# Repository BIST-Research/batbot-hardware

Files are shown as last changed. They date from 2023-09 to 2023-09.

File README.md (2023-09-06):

# batbot-hardware
schematics and pcbs for the batbot

## batbot-6.5 wiring diagram
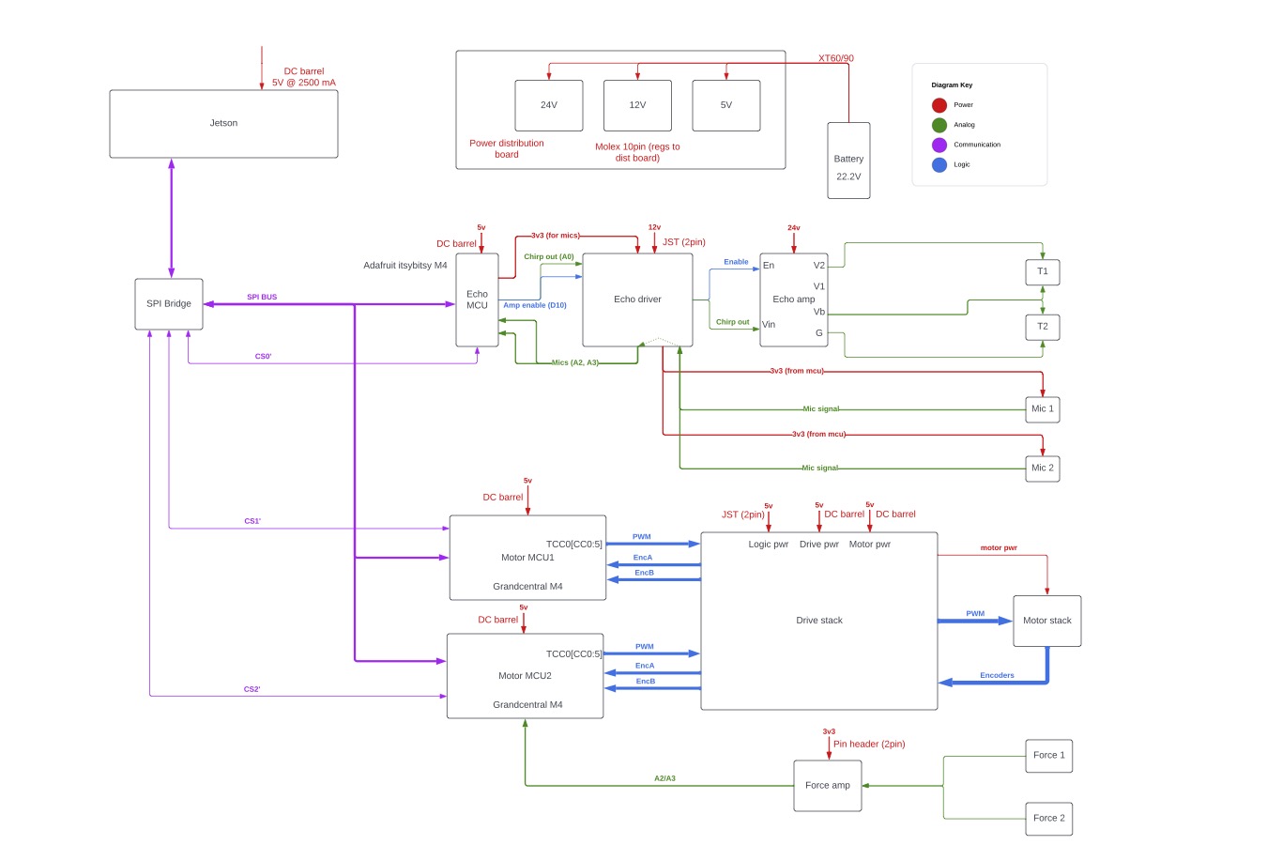
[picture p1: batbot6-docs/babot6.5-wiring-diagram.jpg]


## Adafruit itsybitsy M4 pinout
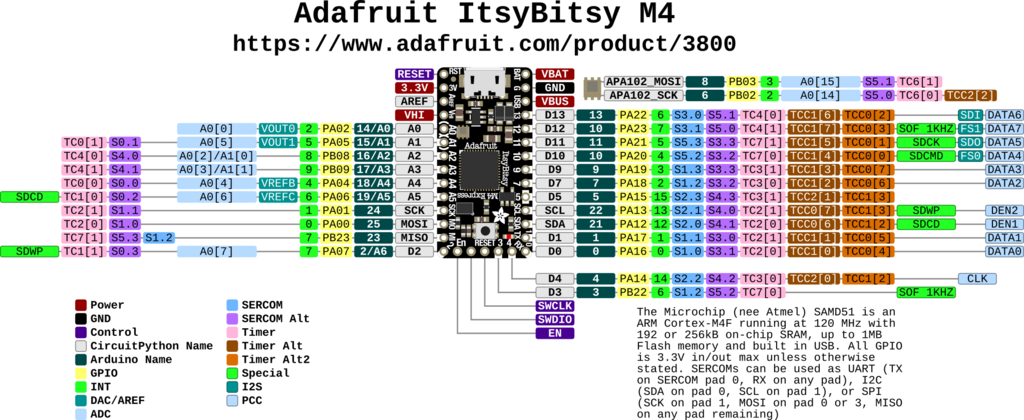
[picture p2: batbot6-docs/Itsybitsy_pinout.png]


## Grandcentral M4 pinout
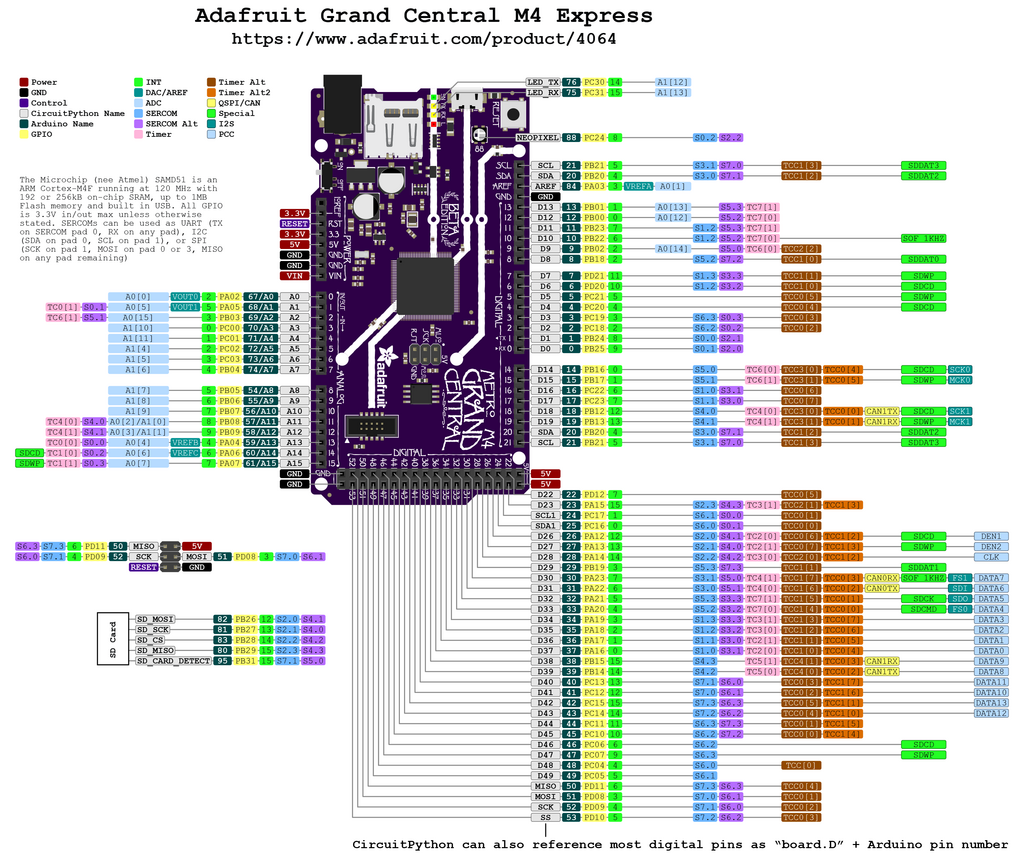
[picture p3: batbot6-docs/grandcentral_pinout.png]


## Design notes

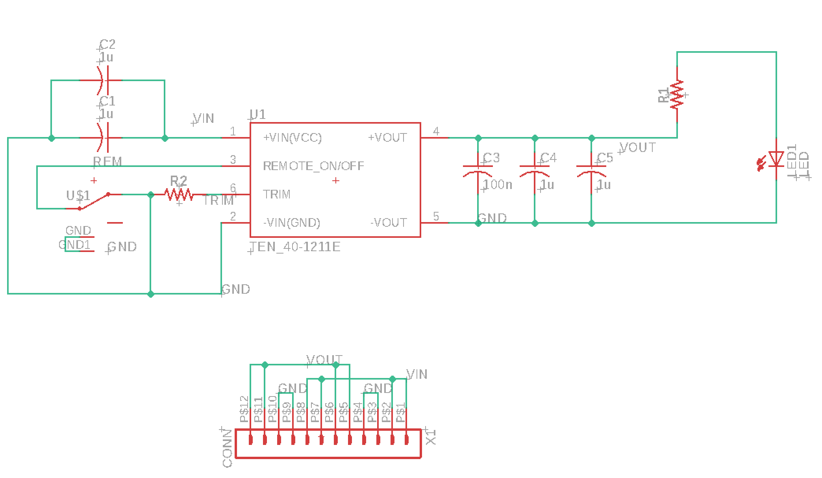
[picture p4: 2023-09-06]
batbot6-power/pc_3v3_rev2/Screen Shot 2023-04-12 at 1.07.49 PM.png

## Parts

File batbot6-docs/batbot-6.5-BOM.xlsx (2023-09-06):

General | Item | Qty | ext price | total price | Link
 | Adafruit Grandcentral M4 | 2 | 39.99 | 79.98 | https://www.adafruit.com/grandcentral
 | Adafruit ItsyBitsy M4 | 1 | 14.95 | 14.95 | https://www.adafruit.com/product/3800
 | Dodotroninc Momimic | 2 | 128.73 | 257.46 | https://www.dodotronic.com/product/momimic/
 | PDm200 V9 | 1 | 296 | 296 | https://www.piezodrive.com/modules/pdm200/
 | 604144 Ultrasonic Transducer | 2 | 30.15 | 60.3 | https://senscomp.com/product/pid-604144-series-600-open-face-ultrasonic-sensor/
 | Nvidia Jetson Nano | 1 | 149 | 149 | https://a.co/d/4efK6vB
 | M2.5 standoff kit | 1 | 14.69 | 14.69 | https://a.co/d/06DHvGg
 | JST male- -> female precrimped kit | 1 | 24.99 | 24.99 | https://a.co/d/bxBMKHO
 | JST female -> female precrimped kit | 1 | 23.99 | 23.99 | https://a.co/d/cVUfNm2
 | JST single ended kit | 1 | 11.99 | 11.99 | https://a.co/d/iteqkm4
Power
 | TEN40-2412E | 1 | 63.89 | 63.89 | https://www.mouser.com/ProductDetail/TRACO-Power/TEN-40-2412E?qs=BJlw7L4Cy78h%252BnAvaMysmw%3D%3D
 | TEN40-2415E | 1 | 62.63 | 62.63 | https://www.mouser.com/ProductDetail/TRACO-Power/TEN-40-2415E?qs=BJlw7L4Cy78izuCDjrMfuQ%3D%3D
 | TEN40-2411E | 1 | 64.85 | 64.85 | https://www.mouser.com/ProductDetail/TRACO-Power/TEN-40-2411E?qs=BJlw7L4Cy79nArvdbUqL%252BA%3D%3D
 | Molex 12 pin female | 3 | 3.9 | 11.7 | https://www.mouser.com/ProductDetail/Molex/44432-1201?qs=WqOAika8Ruu6VDg3%252BKMCCQ%3D%3D
 | Molex 12 pin male | 3 | 5.42 | 16.26 | https://www.mouser.com/ProductDetail/Molex/44764-1201?qs=2RatRY%252BUrpFLNA1OlZuacA%3D%3D
 | XT-60 female | 1 | 1.5 | 1.5 | https://www.mouser.com/ProductDetail/SparkFun/PRT-10474?qs=WyAARYrbSnYJaRDMiD9g2w%3D%3D
 | ZeePower 6000 mAh lipo | 1 | 84.99 | 84.99 | https://a.co/d/9gDvzcF
 | 1825232-1 slide switch | 3 | 0.37 | 1.11 | https://www.mouser.com/ProductDetail/TE-Connectivity-PB/1825232-1?qs=kTKVN3NWb5FosGxaNC1%252BtA%3D%3D
Motors
 | DRV8833 motor driver | 6 | 9.15 | 54.9 | https://www.pololu.com/product/2130
 | 6V 100:1 dc gear motor | 12 | 18.35 | 220.2 | https://www.pololu.com/product/992
 | magnetic encoder pairs | 6 | 7.31 | 43.86 | https://www.pololu.com/product/4760
 | 6 pin female JST SH | 12 | 2.2 | 26.4 | https://www.pololu.com/product/4766
 | JST SH TH breakout adapter | 12 | 1.15 | 13.8 | https://www.pololu.com/product/4772
 | LDTM-028K PVDF | 2 | 6.84 | 13.68 | https://www.mouser.com/ProductDetail/Measurement-Specialties/LDTM-028K?qs=Pz4gaf3%252B8zwC7TEQph04jQ%3D%3D&mgh=1

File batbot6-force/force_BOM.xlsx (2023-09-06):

Desc | Value | Designator | Footprint | part # | type
Cap 50V cer 10% | 10n | C1,C2 | 1206 | C1846 | basic
Cap 50V cer 10% | 100n | C3,C4,C5 | 1206 | C1946 | basic
Res 100mW 1% | 22k | R1,R2 | 0603 | C31850 | basic
Res 100mW 1% | 2k7 | R6,R7 | 0603 | C13167 | basic
Res 100mW 1% | 1Meg | R4,R5,R8,R9 | 0603 | C22935 | basic

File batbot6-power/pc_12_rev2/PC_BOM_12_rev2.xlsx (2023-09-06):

Desc | Value | Designator | Footprint | part # | type
Cap 50V cer 10% | 1u | C1,C2,C4,C5 | 1206 | C1848 | basic
Cap 50V cer 10% | 0u1 | C3 | 1206 | C24497 | basic
Res 250mW 1% | 2k | R1 | 1206 | C17936 | basic
Res 250mW 1% | 200k | R2 | 1206 | C352122 | extended

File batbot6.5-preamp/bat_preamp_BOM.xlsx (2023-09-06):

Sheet: caps
Capacitors
Designator | Value | Package | Tolerance (%) | Usage | Rating (VDC) | ESR (Ohms) | Type | Link
C1 | 10u | 3528 (KEMET-B) | 10 | PSD | 20 | 2.1 | Tantalum | https://www.mouser.com/ProductDetail/KEMET/T491B106K020AT?qs=WydH9nGI6cCRyexXwG9dQg%3D%3D
C2 | 0u1 | 3216 (KEMET-A) | 10 | PSD | 35 | 20 | Tantalum | https://www.mouser.com/ProductDetail/KEMET/T491A104K035AT?qs=VCf6WUQjPgHZen45Mmzj1w%3D%3D
C3 | 0u1 | 3216 (KEMET-A) | 10 | PSD | 35 | 20 | Tantalum | https://www.mouser.com/ProductDetail/KEMET/T491A104K035AT?qs=VCf6WUQjPgHZen45Mmzj1w%3D%3D
C4 | 3u3 | 3216 (KEMET-A) | 10 | PSD | 25 | 0.045 | Tantalum | https://www.mouser.com/ProductDetail/KEMET/T491A335K025AT?qs=PquRuO%2FYcjpqg96tM3ceqQ%3D%3D
C5 | 22u | 6032 (KEMET-C) | 10 | PSD | 25 | 1.4 | Tantalum | https://www.mouser.com/ProductDetail/KEMET/T491C226K025AT
C6 | 0u1 | 3216 (KEMET-A) | 10 | PSD | 35 | 20 | Tantalum | https://www.mouser.com/ProductDetail/KEMET/T491A104K035AT?qs=VCf6WUQjPgHZen45Mmzj1w%3D%3D
C7 | 100n | 0402 | 10 | SIG | 16 | ? | MLCC | https://www.mouser.com/ProductDetail/TDK/C1005X7R1C104K050BC?qs=NRhsANhppD%252BhAGOapA8QKQ%3D%3D
C8 | 100n | 0402 | 10 | SIG | 16 | ? | MLCC | https://www.mouser.com/ProductDetail/TDK/C1005X7R1C104K050BC?qs=NRhsANhppD%252BhAGOapA8QKQ%3D%3D
C9 | 10n | 0402 | 10 | SIG | 25 | ? | MLCC | https://www.mouser.com/ProductDetail/TDK/C1005X7R1E103K050BB?qs=NRhsANhppD8434p4mMcNYg%3D%3D
C10 | 10n | 0402 | 10 | SIG | 25 |  | MLCC | https://www.mouser.com/ProductDetail/TDK/C1005X7R1E103K050BB?qs=NRhsANhppD8434p4mMcNYg%3D%3D

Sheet: diodes
Diodes
Designator | Value | Package | Vf (V) | If (mA) | Usage | Link
D1 | PWR_IND | 1608 | 2 | 20 | LED | https://www.mouser.com/ProductDetail/Wurth-Elektronik/150060AS75003?qs=Li%252BoUPsLEntY15YiEuZJ2w%3D%3D
D2 | JOB_IND | 1608 | 2.85 | 20 | LED | https://www.mouser.com/ProductDetail/Vishay-Semiconductors/VLMTG1400-GS08?qs=gt1LBUVyoHlZ6yHd8iEIzQ%3D%3D

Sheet: conn
Connectors
Designator | Value | Package | Type | Link
J1 | m4_conn_pwr | JST_XH_B4B_Vertical | PWR
J2 | amp_conn_pwr | JST_XH_B4B_Vertical | PWR
J3 | force_conn_in | JST_XH_B4B_Vertical | SIG
J4 | echo_conn_in | JST_XH_B7B_Vertical | SIG
J5 | mic_conn_r | JST_XH_B5B_Vertical | SIG
J6 | mic_conn_l | JST_XH_B5B_Vertical | SIG
J7 | amp_conn_out | JST_XH_B2B_Vertical | SIG
J8 | force_conn_out | JST_XH_B2B_Vertical | SIG

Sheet: res
Resistors
Designator | Value | Package | Tolerance (%) | Rating (W) | Link
R1 | 500R | 3216 | 0.05 | 0.25 | https://www.mouser.com/ProductDetail/Vishay-Draloric/TNPU1206500RAZEN00
R2 | 500R | 3216 | 0.05 | 0.25 | https://www.mouser.com/ProductDetail/Vishay-Draloric/TNPU1206500RAZEN00
R3 | 12k | 3216 | 0.1 | 0.25 | https://www.mouser.com/ProductDetail/Panasonic/ERA-8VRB1202V
R4 | 10k | 3216 | 0.1 | 0.25 | https://www.mouser.com/ProductDetail/Panasonic/ERA-8VRB1002V
R5 | 39k | 3216 | 0.1 | 0.25 | https://www.mouser.com/ProductDetail/Panasonic/ERA-8VRB3902V
R6 | 27k | 3216 | 0.1 | 0.25 | https://www.mouser.com/ProductDetail/Panasonic/ERA-8VRB2702V
R7 | 10k | 3216 | 0.1 | 0.25 | https://www.mouser.com/ProductDetail/Panasonic/ERA-8VRB1002V
R8 | 100k | 3216 | 0.1 | 0.25 | https://www.mouser.com/ProductDetail/Panasonic/ERA-8VRB1003V
R9 | 2k7 | 3216 | 0.1 | 0.25 | https://www.mouser.com/ProductDetail/Panasonic/ERA-8ARB272V
R10 | 2k7 | 3216 | 0.1 | 0.25 | https://www.mouser.com/ProductDetail/Panasonic/ERA-8ARB272V
R11 | 1Meg | 3216 | 0.1 | 0.25 | https://www.mouser.com/ProductDetail/Panasonic/ERA-8AED105V
R12 | 1Meg | 3216 | 0.1 | 0.25 | https://www.mouser.com/ProductDetail/Panasonic/ERA-8AED105V
R13 | 22k | 3216 | 0.1 | 0.25 | https://www.mouser.com/ProductDetail/Panasonic/ERA-8AEB223V
R14 | 22k | 3216 | 0.1 | 0.25 | https://www.mouser.com/ProductDetail/Panasonic/ERA-8AEB223V

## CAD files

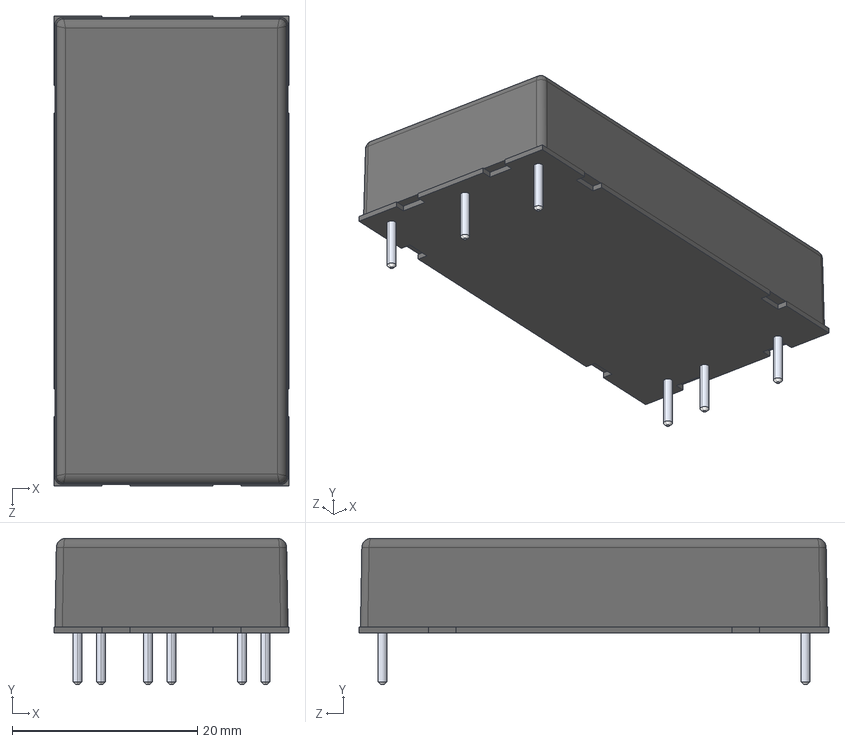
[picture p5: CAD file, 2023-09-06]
batbot6.5-power/TEN_40-2410E/TEN_40-2410E.step
25.4 x 15.8 x 50.8 mm

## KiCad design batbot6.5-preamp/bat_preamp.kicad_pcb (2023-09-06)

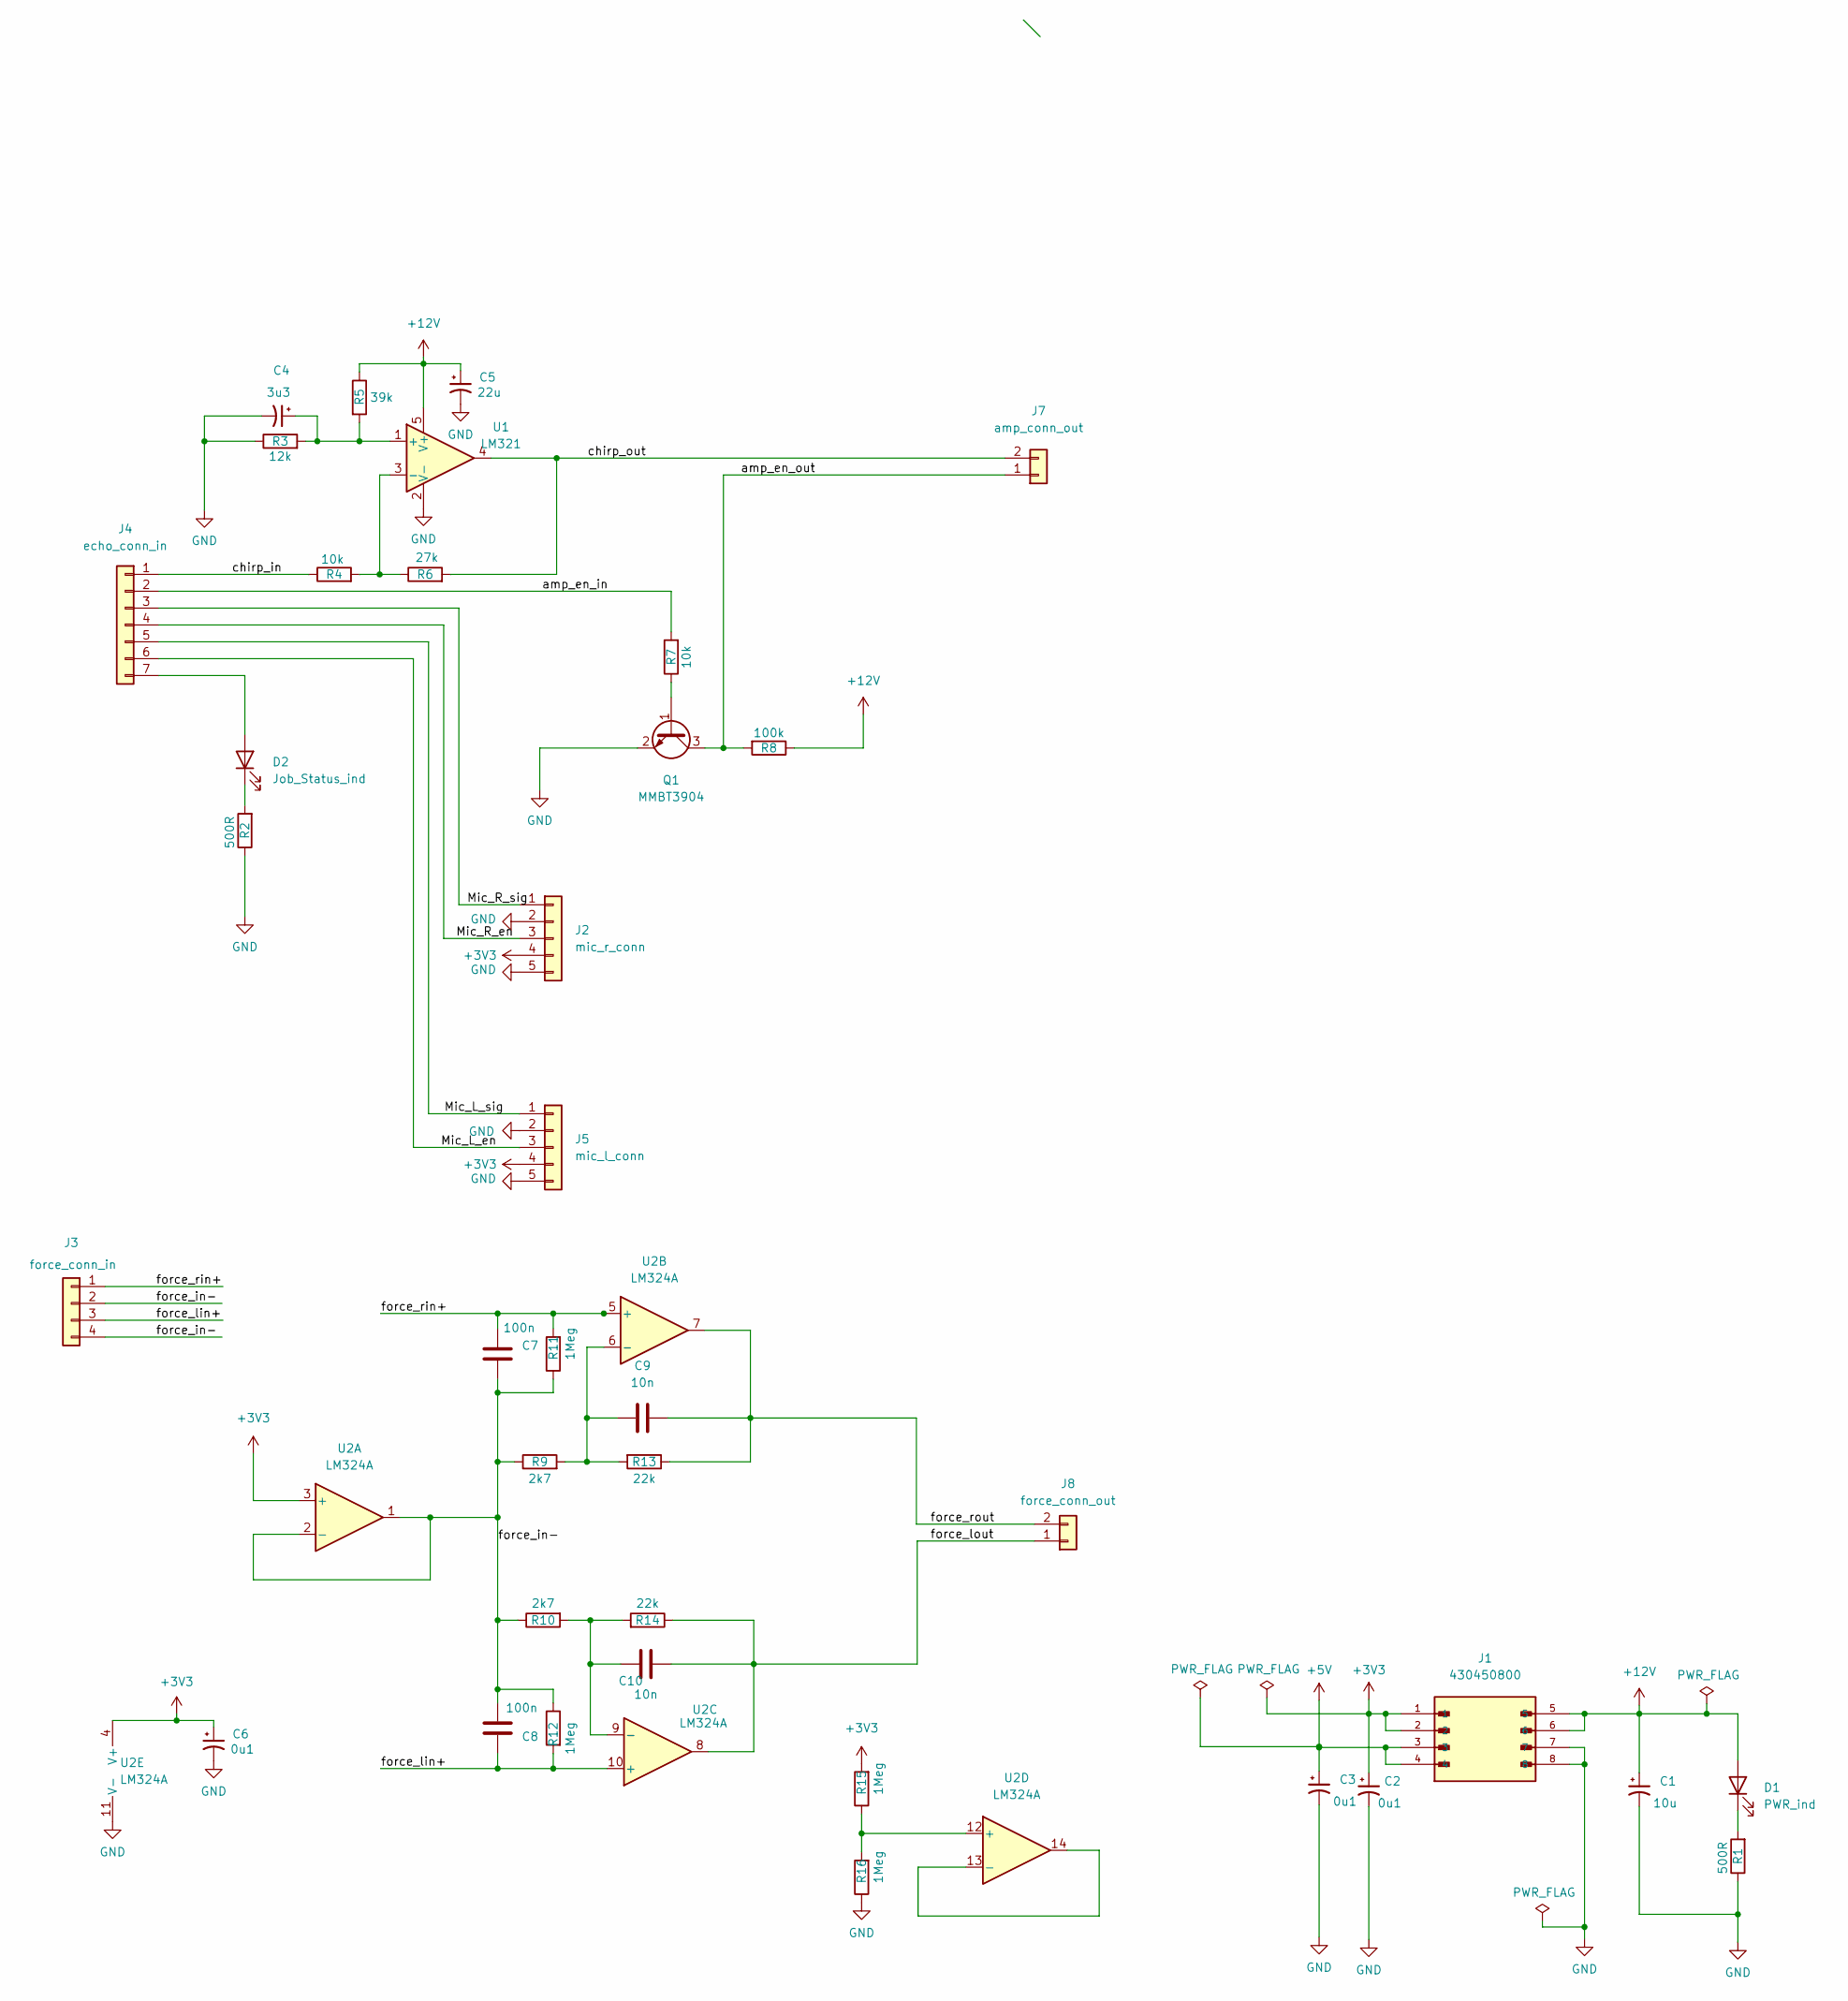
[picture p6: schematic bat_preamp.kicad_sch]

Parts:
C1: 10u; CP_EIA-3528-21_Kemet-B_Pad1.50x2.35mm_HandSolder
C2, C3: 0u1; CP_EIA-3216-18_Kemet-A_Pad1.58x1.35mm_HandSolder
C4: 3u3; CP_EIA-3216-18_Kemet-A_Pad1.58x1.35mm_HandSolder
C5: 22u; CP_EIA-3216-18_Kemet-A_Pad1.58x1.35mm_HandSolder
C6: 0u1; CP_EIA-6032-28_Kemet-C_Pad2.25x2.35mm_HandSolder
C7, C8: 100n; C_0402_1005Metric_Pad0.74x0.62mm_HandSolder
C9, C10: 10n; C_0402_1005Metric_Pad0.74x0.62mm_HandSolder
D1: PWR_ind; LED_0603_1608Metric_Pad1.05x0.95mm_HandSolder
D2: Job_Status_ind; LED_0603_1608Metric_Pad1.05x0.95mm_HandSolder
J1: 430450800; MOLEX_430450800; PARTREV G
J2: mic_r_conn; JST_XH_B5B-XH-A_1x05_P2.50mm_Vertical
J3: force_conn_in; JST_XH_B4B-XH-A_1x04_P2.50mm_Vertical
J4: echo_conn_in; JST_XH_B7B-XH-A_1x07_P2.50mm_Vertical
J5: mic_l_conn; JST_XH_B5B-XH-A_1x05_P2.50mm_Vertical
J7: amp_conn_out; JST_XH_B2B-XH-A_1x02_P2.50mm_Vertical
J8: force_conn_out; JST_XH_B2B-XH-A_1x02_P2.50mm_Vertical
Q1: MMBT3904; SOT-23
R1, R2: 500R; R_1206_3216Metric_Pad1.30x1.75mm_HandSolder
R3: 12k; R_0603_1608Metric_Pad0.98x0.95mm_HandSolder
R4: 10k; R_1206_3216Metric_Pad1.30x1.75mm_HandSolder
R5: 39k; R_0603_1608Metric_Pad0.98x0.95mm_HandSolder
R6: 27k; R_1206_3216Metric_Pad1.30x1.75mm_HandSolder
R7: 10k; R_0603_1608Metric_Pad0.98x0.95mm_HandSolder
R8: 100k; R_1206_3216Metric_Pad1.30x1.75mm_HandSolder
R9, R10: 2k7; R_0603_1608Metric_Pad0.98x0.95mm_HandSolder
R11, R12, R15, R16: 1Meg; R_0603_1608Metric_Pad0.98x0.95mm_HandSolder
R13, R14: 22k; R_0603_1608Metric_Pad0.98x0.95mm_HandSolder
U1: LM321; SOT-23-5
U2: LM324A; SOIC-14_3.9x8.7mm_P1.27mm

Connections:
+3V3: C2.1, C6.1, J1.1, J1.2, J2.4, J5.4, R15.2, U2.3 (+), U2.4 (V+)
+5V: C3.1, J1.3, J1.4
+12V: C1.1, C5.1, D1.2 (A), J1.5, J1.6, R5.1, R8.1, U1.5 (V+)
/Mic_L_en: J4.6, J5.3
/Mic_L_sig: J4.5, J5.1
/Mic_R_en: J2.3, J4.4
/Mic_R_sig: J2.1, J4.3
/amp_en_in: J4.2, R7.2
/amp_en_out: J7.1, Q1.3 (C), R8.2
/chirp_in: J4.1, R4.1
/chirp_out: J7.2, R6.2, U1.4
/force_in-: C7.2, C8.2, J3.2, J3.4, R9.1, R10.1, R11.1, R12.1, U2.1, U2.2 (-)
/force_lin+: C8.1, J3.3, R12.2, U2.10 (+)
/force_lout: C10.2, J8.1, R14.1, U2.8
/force_rin+: C7.1, J3.1, R11.2, U2.5 (+)
/force_rout: C9.2, J8.2, R13.1, U2.7
GND: C1.2, C2.2, C3.2, C4.2, C5.2, C6.2, J1.7, J1.8, J2.2, J2.5, J5.2, J5.5, Q1.2 (E), R1.1, R2.1, R3.1, R16.1, U1.2 (V-), U2.11 (V-)
unnamed: C4.1, R3.2, R5.2, U1.1 (+)
unnamed: C9.1, R9.2, R13.2, U2.6 (-)
unnamed: C10.1, R10.2, R14.2, U2.9 (-)
unnamed: D1.1 (K), R1.2
unnamed: D2.1 (K), R2.2
unnamed: D2.2 (A), J4.7
unnamed: Q1.1 (B), R7.1
unnamed: R4.2, R6.1, U1.3 (-)
unnamed: R15.1, R16.2, U2.12 (+)
unnamed: U2.13 (-), U2.14

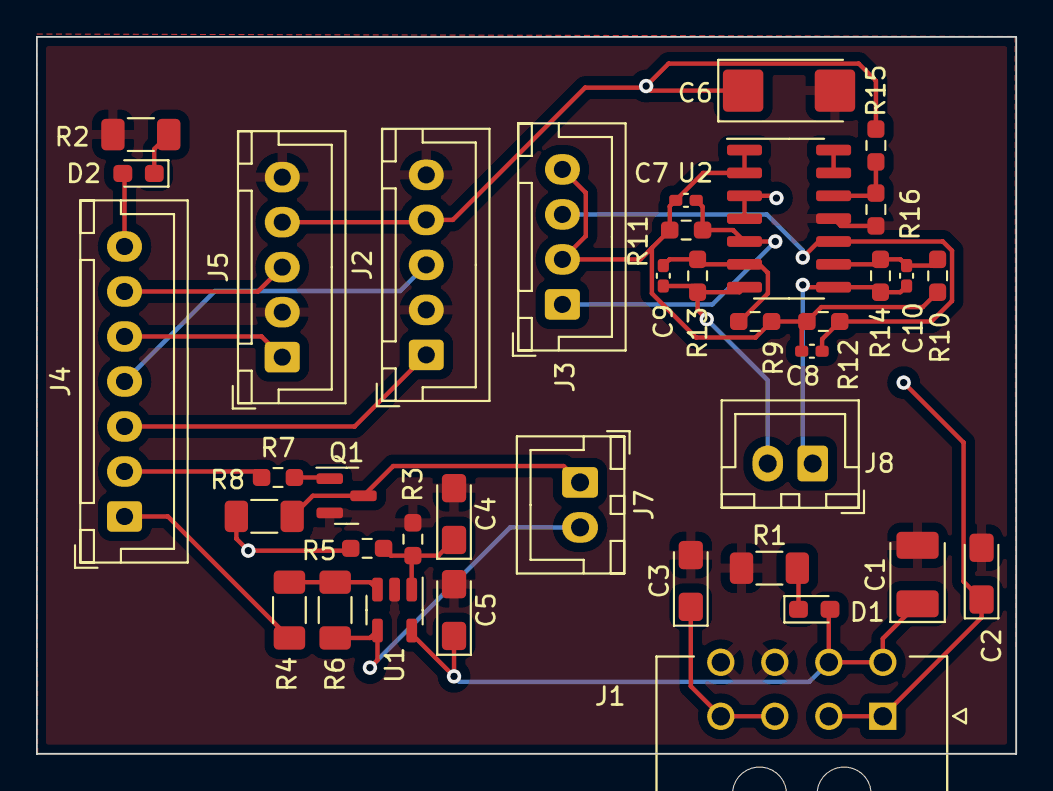
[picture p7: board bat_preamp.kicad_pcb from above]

Board: 2 copper layers, 54.4 x 39.8 mm, 38 parts (0 on the bottom side), 27 nets.

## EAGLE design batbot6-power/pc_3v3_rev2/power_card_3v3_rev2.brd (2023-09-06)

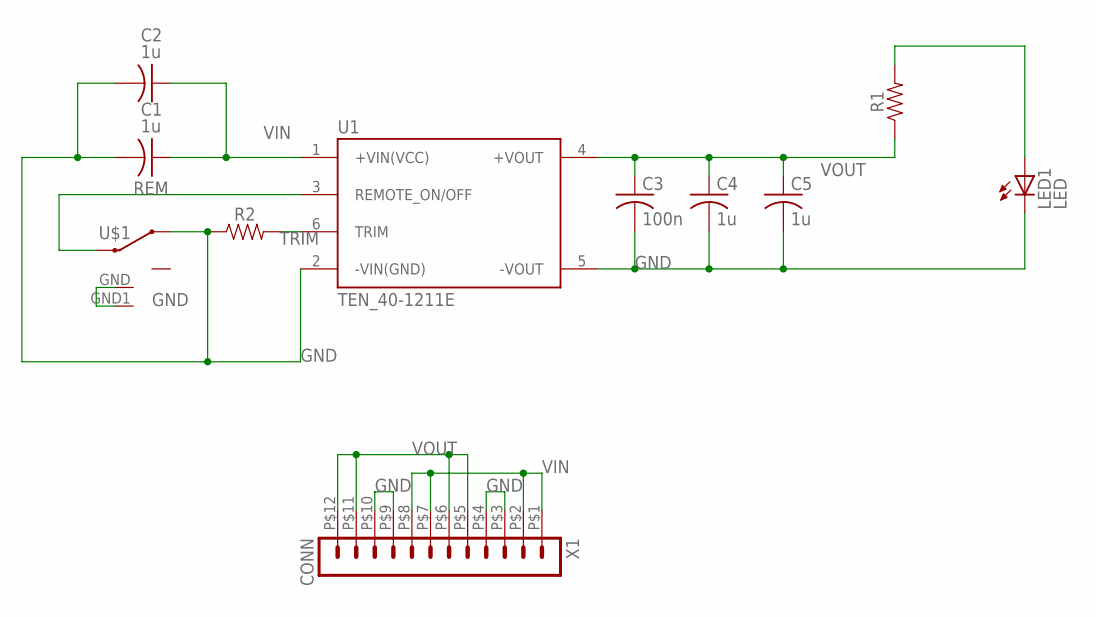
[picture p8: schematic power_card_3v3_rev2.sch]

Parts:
C1, C2, C4, C5: 1u; C1206
C3: 100n; C1206
LED1: LED; LED5MM
R1, R2: 1206
U1: TEN_40-1211E; CONV_TEN_40-1211E
U$1: 1825232-1
X1: CONN; 44764-1201

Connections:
GND: C1.2, C2.2, C3.2, C4.2, C5.2, LED1.K (C), R2.1, U1.2 (-VIN(GND)), U1.5 (-VOUT), U$1.3, U$1.GND, U$1.GND1, X1.P$3 (3), X1.P$4 (4), X1.P$9 (9), X1.P$10 (10)
unnamed: LED1.A, R1.2
REM: U1.3 (REMOTE_ON/OFF), U$1.2
TRIM: R2.2, U1.6 (TRIM)
VIN: C1.1, C2.1, U1.1 (+VIN(VCC)), X1.P$1 (1), X1.P$2 (2), X1.P$7 (7), X1.P$8 (8)
VOUT: C3.1, C4.1, C5.1, R1.1, U1.4 (+VOUT), X1.P$5 (5), X1.P$6 (6), X1.P$11 (11), X1.P$12 (12)

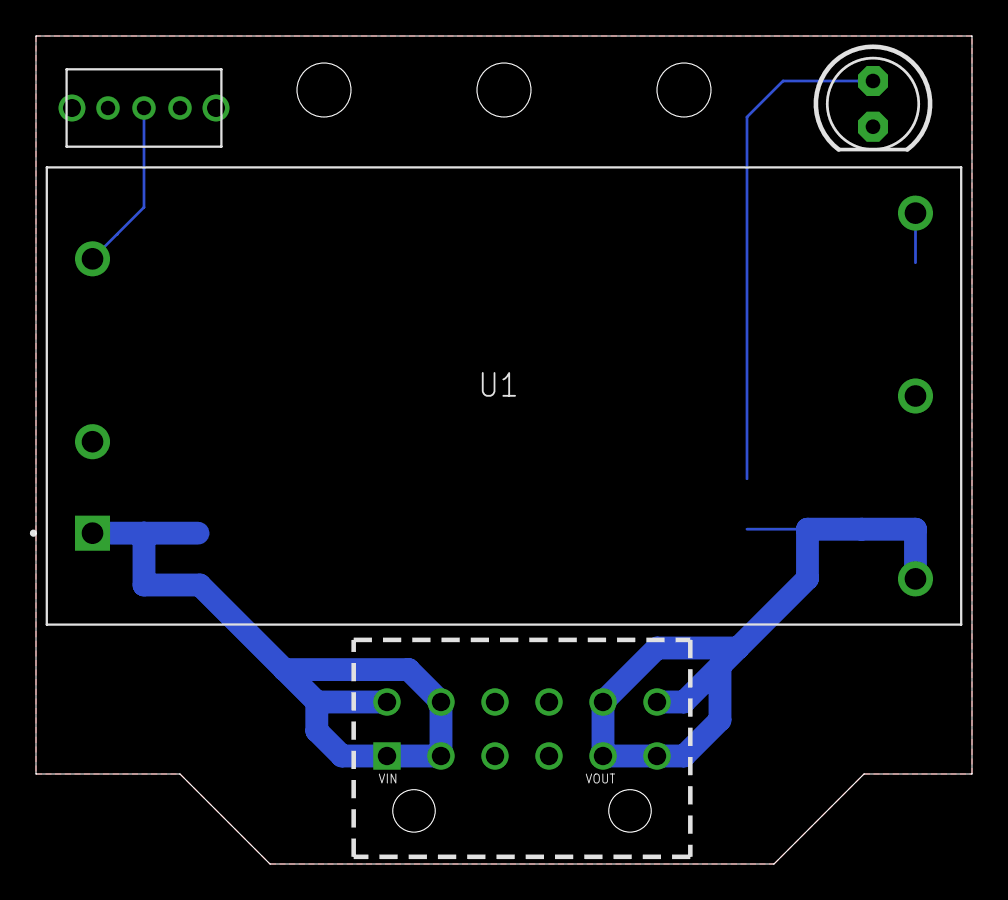
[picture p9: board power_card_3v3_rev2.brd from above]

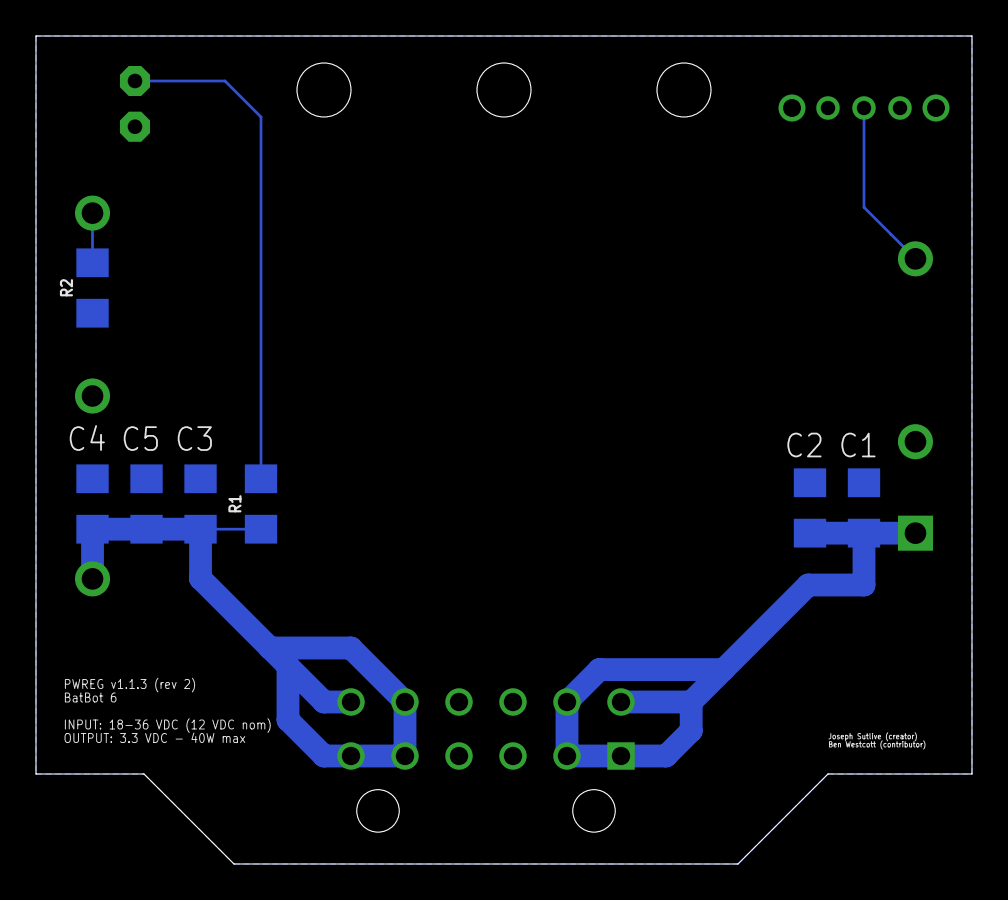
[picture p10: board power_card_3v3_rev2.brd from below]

Board: 2 copper layers, 52.0 x 46.0 mm, 11 parts (7 on the bottom side), 6 nets.

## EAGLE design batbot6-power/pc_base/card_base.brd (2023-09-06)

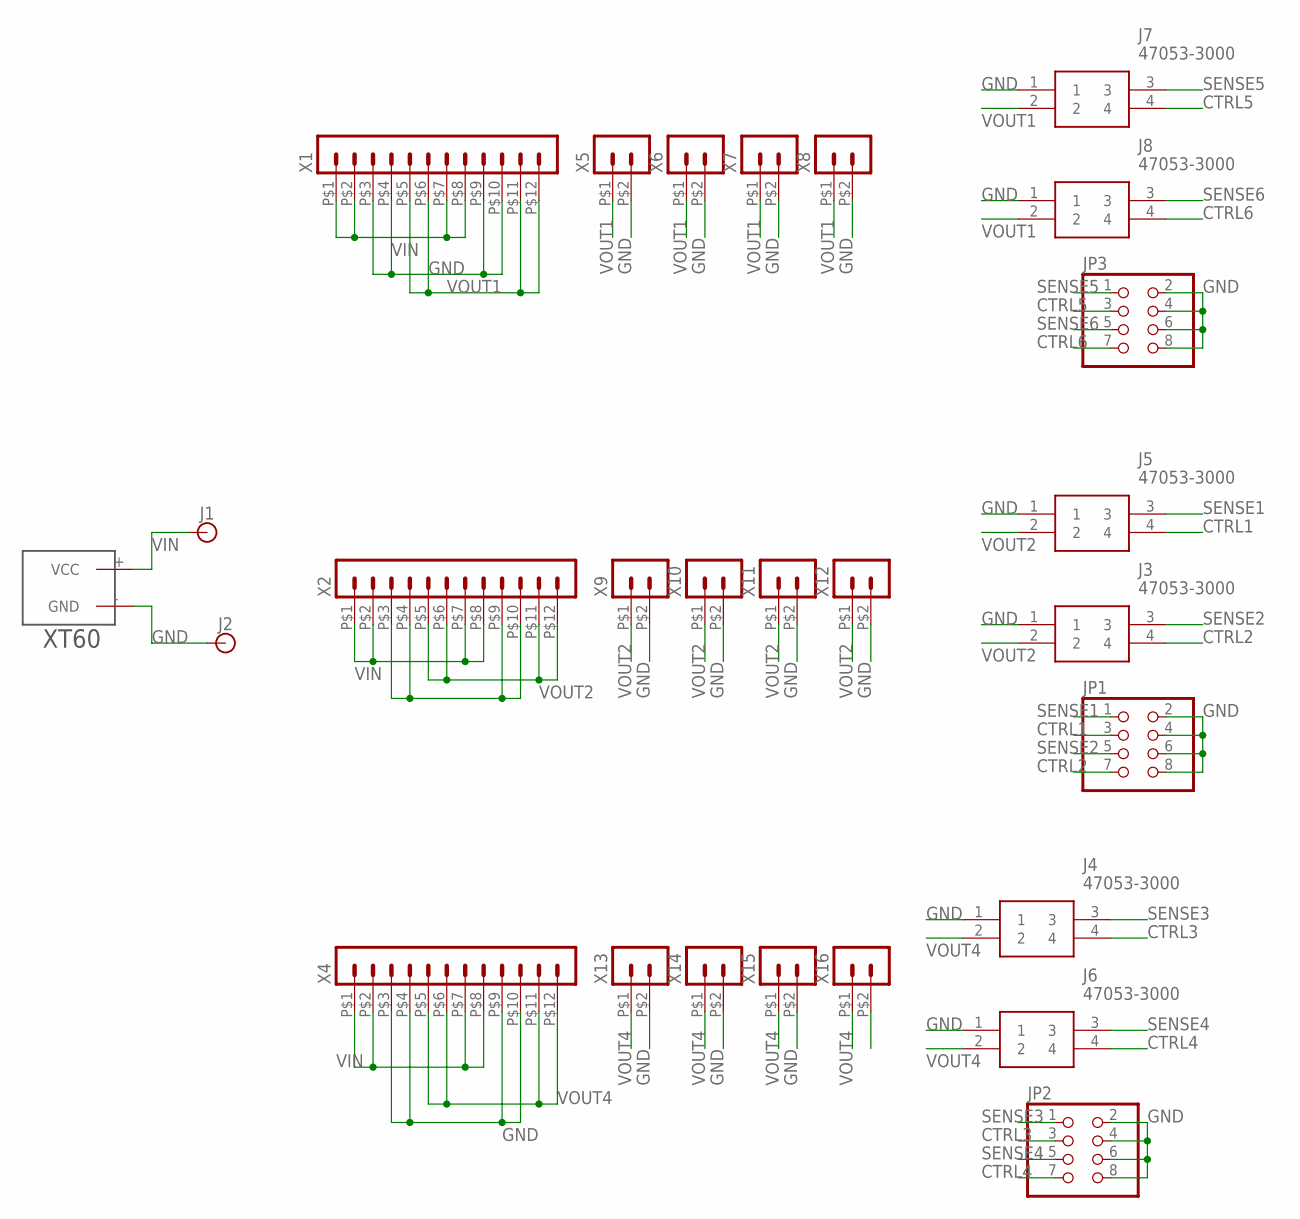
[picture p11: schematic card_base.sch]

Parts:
J1, J2: BANANA_CONN
J3, J4, J5, J6, J7, J8: 47053-3000; 470533000
JP1, JP2, JP3: PINHD-2X4; 2X04
U$1: XT60
X1, X2, X4: HEADER_POS12_44432-1201; 44432-1201
X5, X6, X7, X8, X9, X10, X11, X12, X13, X14, X15, X16: HEADER_POS2_44914-0201; 44914-0201

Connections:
CTRL1: J5.4, JP1.3
CTRL2: J3.4, JP1.7
CTRL3: J4.4, JP2.3
CTRL4: J6.4, JP2.7
CTRL5: J7.4, JP3.3
CTRL6: J8.4, JP3.7
GND: J2.P$1, J3.1, J4.1, J5.1, J6.1, J7.1, J8.1, JP1.2, JP1.4, JP1.6, JP1.8, JP2.2, JP2.4, JP2.6, JP2.8, JP3.2, JP3.4, JP3.6, JP3.8, U$1.- (GND), X1.P$3 (3), X1.P$4 (4), X1.P$9 (9), X1.P$10 (10), X2.P$3 (3), X2.P$4 (4), X2.P$9 (9), X2.P$10 (10), X4.P$3 (3), X4.P$4 (4), X4.P$9 (9), X4.P$10 (10), X5.P$2 (2), X6.P$2 (2), X7.P$2 (2), X8.P$2 (2), X9.P$2 (2), X10.P$2 (2), X11.P$2 (2), X12.P$2 (2), X13.P$2 (2), X14.P$2 (2), X15.P$2 (2), X16.P$2 (2)
SENSE1: J5.3, JP1.1
SENSE2: J3.3, JP1.5
SENSE3: J4.3, JP2.1
SENSE4: J6.3, JP2.5
SENSE5: J7.3, JP3.1
SENSE6: J8.3, JP3.5
VIN: J1.P$1, U$1.+ (VCC), X1.P$1 (1), X1.P$2 (2), X1.P$7 (7), X1.P$8 (8), X2.P$1 (1), X2.P$2 (2), X2.P$7 (7), X2.P$8 (8), X4.P$1 (1), X4.P$2 (2), X4.P$7 (7), X4.P$8 (8)
VOUT1: J7.2, J8.2, X1.P$5 (5), X1.P$6 (6), X1.P$11 (11), X1.P$12 (12), X5.P$1 (1), X6.P$1 (1), X7.P$1 (1), X8.P$1 (1)
VOUT2: J3.2, J5.2, X2.P$5 (5), X2.P$6 (6), X2.P$11 (11), X2.P$12 (12), X9.P$1 (1), X10.P$1 (1), X11.P$1 (1), X12.P$1 (1)
VOUT4: J4.2, J6.2, X4.P$5 (5), X4.P$6 (6), X4.P$11 (11), X4.P$12 (12), X13.P$1 (1), X14.P$1 (1), X15.P$1 (1), X16.P$1 (1)

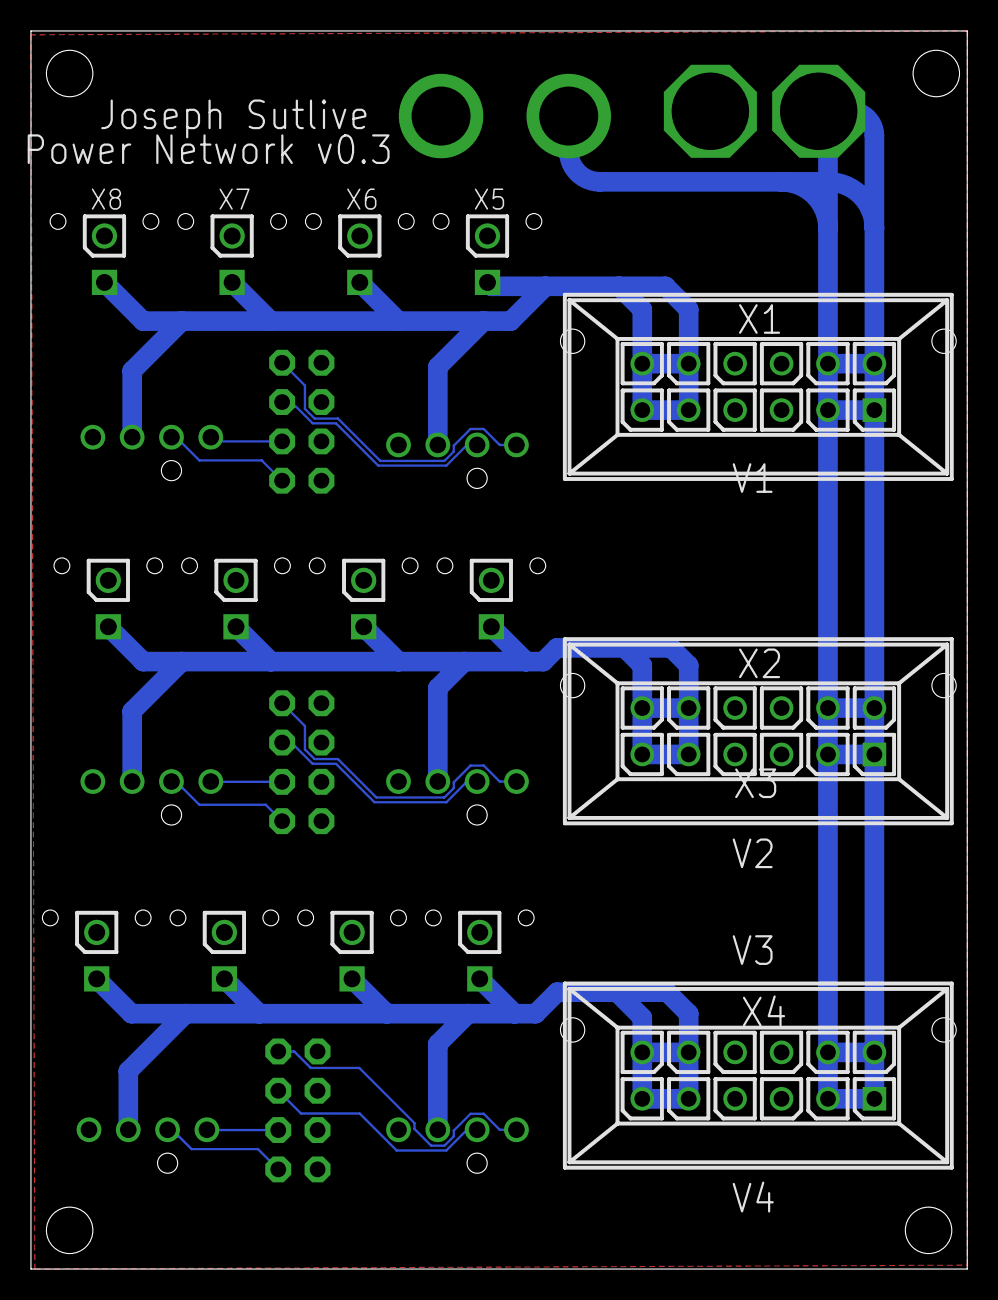
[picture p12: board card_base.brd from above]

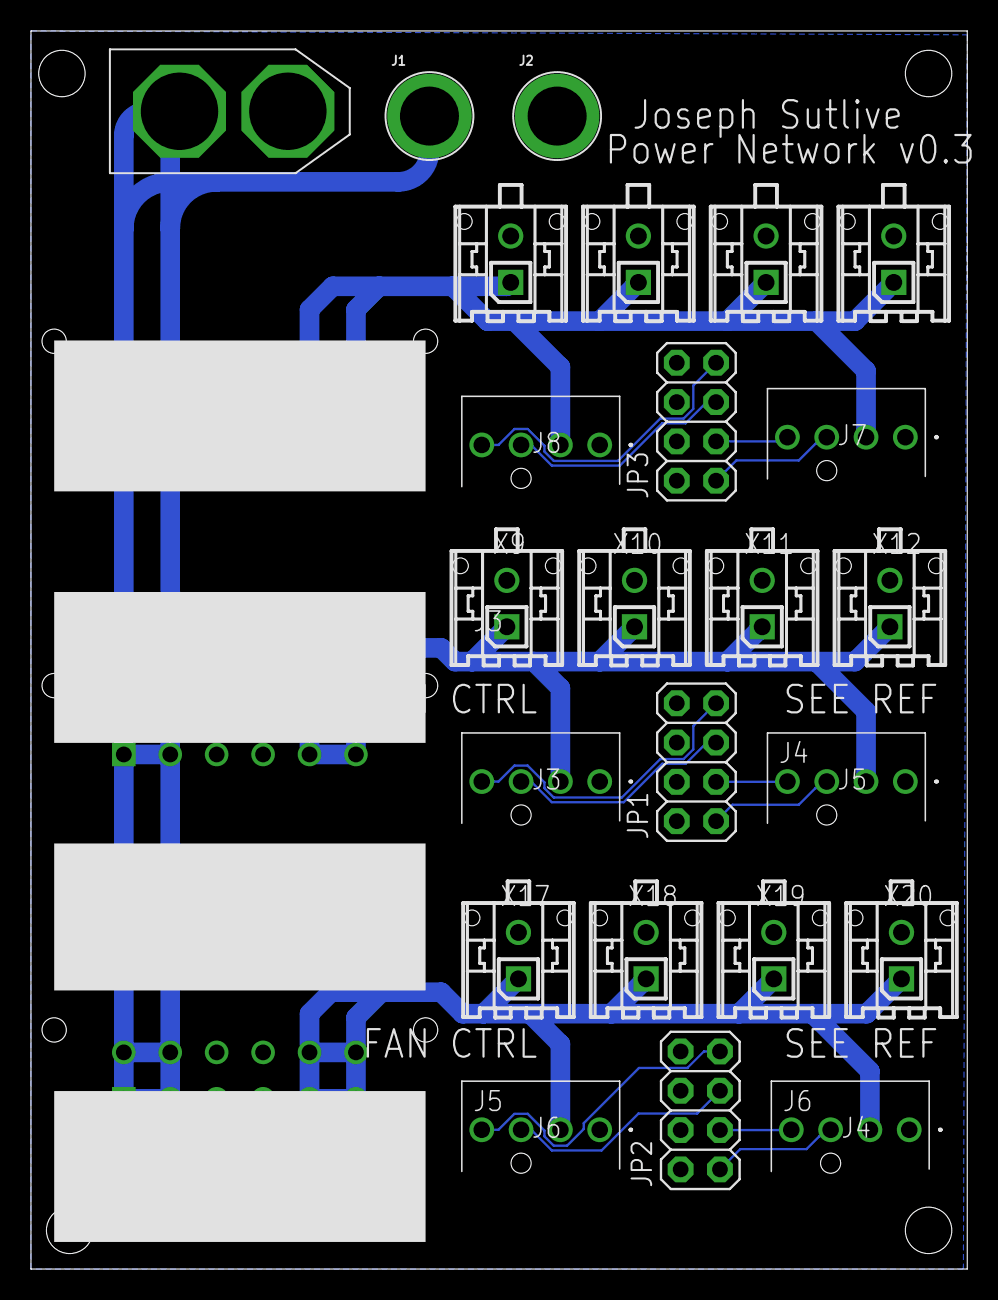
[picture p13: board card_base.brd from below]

Board: 2 copper layers, 60.5 x 80.0 mm, 27 parts (24 on the bottom side), 17 nets.

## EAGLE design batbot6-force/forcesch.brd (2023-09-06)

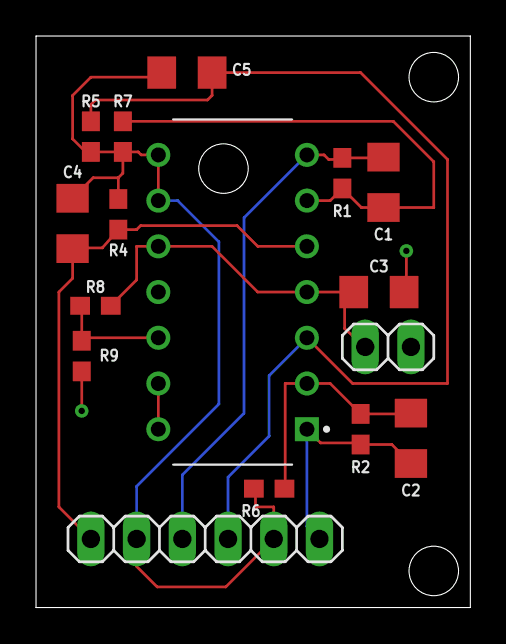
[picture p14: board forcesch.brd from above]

Board: 2 copper layers, 24.1 x 31.8 mm, 16 parts (0 on the bottom side), 11 nets.

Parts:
C1, C2: 10n; 1206
C3: 0u1; 1206
C4, C5: 100n; 1206
JP1: 1X02
JP4: 1X06
R1, R2: 22k; 0603
R4, R5, R8, R9: 1Meg; 0603
R6, R7: 2k7; 0603
U$1: LM324N/NOPB; DIP825W47P254L1917H533Q14

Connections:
GND: C3.2, JP1.2, R9.1, U$1.11
L-: C2.1, R2.2, R6.2, U$1.2
LIN+: C5.2, JP4.4, R5.1, U$1.3
LOUT: C2.2, JP4.6, R2.1, U$1.1
unnamed: U$1.13, U$1.14
unnamed: R8.1, R9.2, U$1.12
R-: C1.2, R1.1, R7.2, U$1.6
RIN+: C4.1, JP4.1, R4.2, U$1.5
RLIN-: C4.2, C5.1, JP4.2, JP4.5, R4.1, R5.2, R6.1, R7.1, U$1.8, U$1.9
ROUT: C1.1, JP4.3, R1.2, U$1.7
VCC: C3.1, JP1.1, R8.2, U$1.4, U$1.10

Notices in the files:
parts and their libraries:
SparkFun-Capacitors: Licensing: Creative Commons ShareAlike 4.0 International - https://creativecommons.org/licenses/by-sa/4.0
